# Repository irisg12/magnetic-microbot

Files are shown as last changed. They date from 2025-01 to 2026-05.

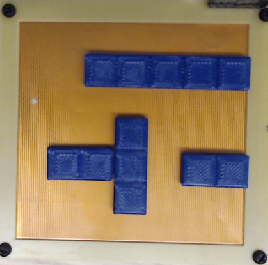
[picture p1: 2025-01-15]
MATLAB/TeamImage2.png

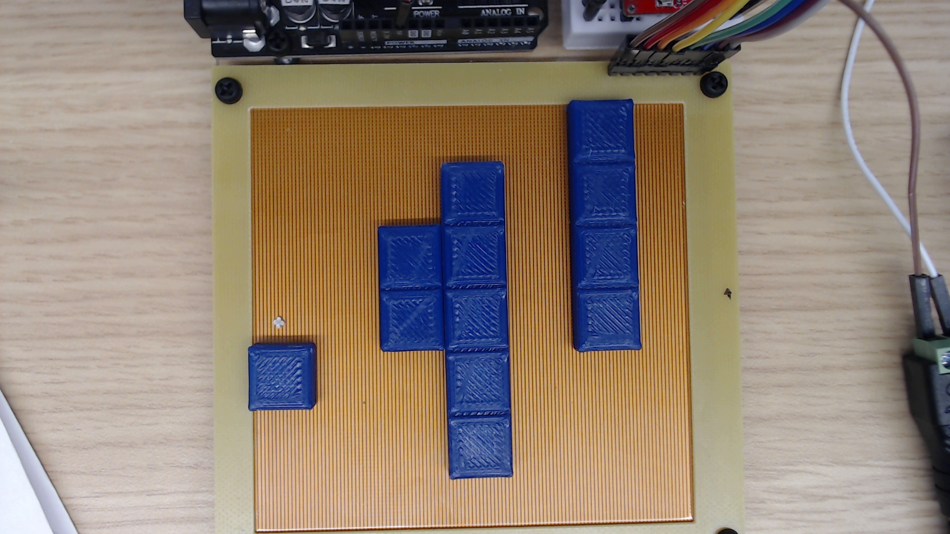
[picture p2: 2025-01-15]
MATLAB/TeamImage1.jpg

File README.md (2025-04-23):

# magnetic-microrobot

Magnetic microrobot manipulation system that adapts a flex PCB platform inspired by the Hackaday “2D Stepper Motor Etched on PCB” project.

## Overview

This repository contains code, schematics, and CAD files for a mm-scale magnetic robot control platform designed for open and closed loop trajectory execution, computer vision robot tracking, and micromanipulation.

The system uses a two-layer flex PCB with orthogonal serpentine traces powered by two stepper motor drivers. The resulting configuration generates magnetic fields that allow a mm-scale magnet placed on the PCB to be manipulated in 8 directions. 

## Features 

- Live tracking of robot and obstacle positions for closed-loop control and image processing
- Direction control and motor driver actuation via Arduino serial communication
- MATLAB A* pathfinding algorithm and visualization for trajectory planning and obstacle avoidance 

### Included Files

- FLEX PCB Gerber Files for manufacturing
- DXF file for acrylic base with cutouts for PCB mounting and wiring
- STL files for obstacles and manipulation payloads 

## Requirements

- MATLAB Support Package for USB Webcams
- MATLAB Image Processing Toolbox

## File Organization

- Upload microbot_multidirection_serial.ino to Arduino Uno

## Hardware Components 

- Flex PCB with stiffener
- N52 disk magnets: 1mm x 0.5mm (4 ct) and 3mm x 1mm (1 ct)
- Arduino Uno
- 170 pin breadboard
- A4988 Stepper Motor Drivers (2 ct)
- 3/16" thick acrylic sheet: each base has approximate dimensions 4.2" x 5.9" 
- M3 nuts and bolts for mounting 
- Webcam & webcam stand

## Wiring Schematic
Default pin connections for Arduino, motor drivers, and PCB also available in SetupSchematic.svg. Drivers are full-stepping, which results in the smoothest motion.

Schematic

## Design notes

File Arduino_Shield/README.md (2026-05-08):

# Arduino shield for platform system

This folder contains relevant files for an Arduino motor shield to control each platform.

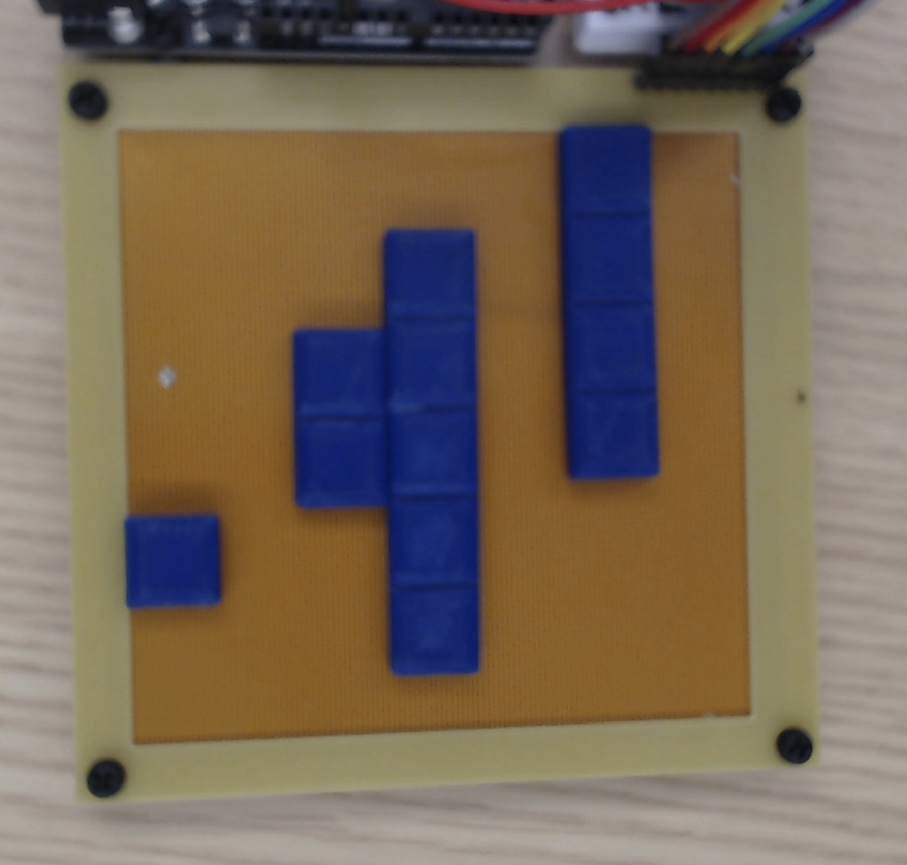
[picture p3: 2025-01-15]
MATLAB/TeamImage3.jpg

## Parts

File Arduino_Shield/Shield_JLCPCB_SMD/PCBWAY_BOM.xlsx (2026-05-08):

 |  |  | xxxx xxxx xxxxx xxPCS BOM (Sample Bill of Materials)
Item # | *Designator | *Qty | Manufacturer | *Mfg Part # | Description / Value | *Package/Footprint | Type | Your Instructions / Notes | LCSC Number
1 | C4,C3 | 2 | Honor Elec | RVT1E101M0607 | CAP-SMD_BD6.3-L6.6-W6.6-LS7.2-R-RD | SMD | SMD | 100uF | C3338
2 | J1,J4 | 2 | SparkFun | PRT-11417 | PinSocket_1x08_P2.54mm_Vertical | 8POS | thru-hole | Arduino Header Kit - Power
3 | J3 | 1 | SparkFun | PRT-11417 | PinSocket_1x06_P2.54mm_Vertical | 6POS | thru-hole | Arduino Header Kit - Analog
4 | J2 | 1 | SparkFun | PRT-11417 | PinSocket_1x10_P2.54mm_Vertical | 10POS | thru-hole | Arduino Header Kit - Digita/PWM
5 | C1,C2 | 2 | Samsung Electro-Mechanics | CL21B104KCFNNNE | C_0805_2012Metric | 0805 | SMD | .1uF | C28233
6 | J5 | 1 | XKB Connection | DC-018-2.5A-2.5 | DC-IN-TH_DC-018 |  | thru-hole | Barrel Jack | C2880553
7 | LR1,LR2,UD2,UD1 | 4 | BOOMELE | 2.54-1*8P | PinSocket_1x08_P2.54mm_Vertical | 8POS | thru-hole | 1x8 | C27438
8 | X1,Y1 | 2 | XFCN | PZ254V-11-04P | PinHeader_1x04_P2.54mm_Vertical | 4POS | thru-hole | 1x4 Pin | C492403

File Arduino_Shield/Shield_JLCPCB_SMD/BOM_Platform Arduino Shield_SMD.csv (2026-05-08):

Id | Designator | Footprint | Quantity | Designation | Supplier and ref
1 | C4,C3 | C_1206_3216Metric | 2 | 100uF
2 | J1 | PinSocket_1x08_P2.54mm_Vertical | 1 | Power
3 | J3 | PinSocket_1x06_P2.54mm_Vertical | 1 | Analog
4 | J2 | PinSocket_1x10_P2.54mm_Vertical | 1 | Digital/PWM
5 | J4 | PinSocket_1x08_P2.54mm_Vertical | 1 | Digital/PWM
6 | C1,C2 | C_0805_2012Metric | 2 | .1uF
7 | J5 | BarrelJack_Horizontal | 1 | Barrel_Jack_MountingPin
8 | LR1,LR2,UD2,UD1 | PinSocket_1x08_P2.54mm_Vertical | 4 | Conn_01x08
9 | X1,Y1 | PinHeader_1x04_P2.54mm_Vertical | 2 | Conn_01x04_Pin

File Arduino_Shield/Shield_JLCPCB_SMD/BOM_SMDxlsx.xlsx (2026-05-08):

Id | Designator | Footprint | Quantity | Designation | JLCPCB Part #
1 | C4,C3 | CAP-SMD_BD6.3-L6.6-W6.6-LS7.2-R-RD | 2 | 100uF | C3338
2 | J1,J4 | PinSocket_1x08_P2.54mm_Vertical | 1 | Power | C27438
3 | J3 | PinSocket_1x06_P2.54mm_Vertical | 1 | Analog | C2935900
4 | J2 | PinSocket_1x10_P2.54mm_Vertical | 1 | Digital/PWM | C350306
5 | C1,C2 | C_0805_2012Metric | 2 | .1uF | C28233
6 | J5 | DC-IN-TH_DC-018 | 1 | Barrel_Jack_MountingPin | C2880553
7 | LR1,LR2,UD2,UD1 | PinSocket_1x08_P2.54mm_Vertical | 4 | Conn_01x08 | C27438
8 | X1,Y1 | PinHeader_1x04_P2.54mm_Vertical | 2 | Conn_01x04_Pin | C492403

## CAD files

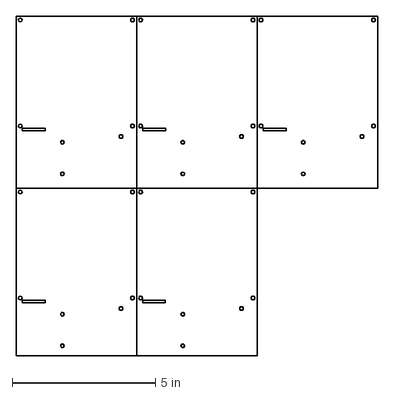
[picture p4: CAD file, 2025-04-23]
Acrylic Laser Cut 5ct - Iris.dxf
12.6 x 11.8 in

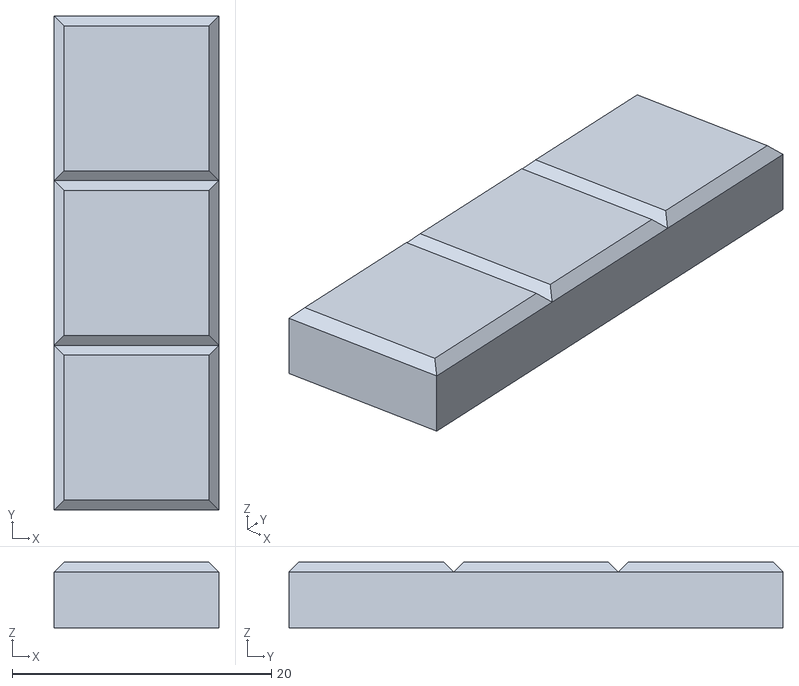
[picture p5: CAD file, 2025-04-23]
CAD_Models/obstacle_3bit.stl
12.7 x 38.1 x 5.08

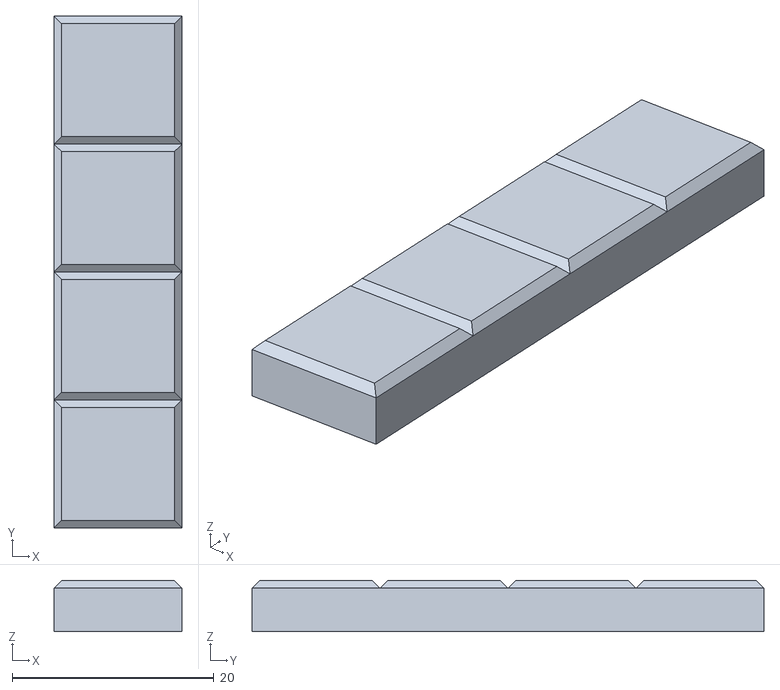
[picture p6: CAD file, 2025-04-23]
CAD_Models/obstacle_4bit.stl
12.7 x 50.8 x 5.08

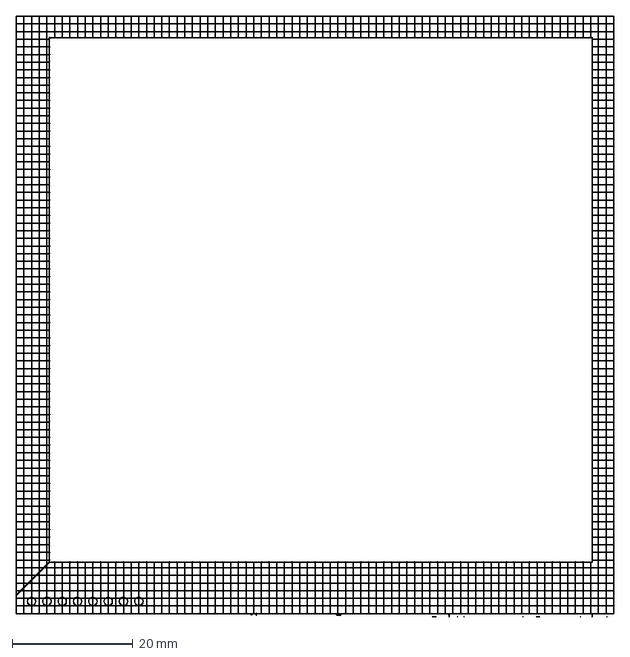
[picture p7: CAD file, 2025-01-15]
FLEX PCB Stiffener Border DXF.dxf
99.1 x 99.7 mm

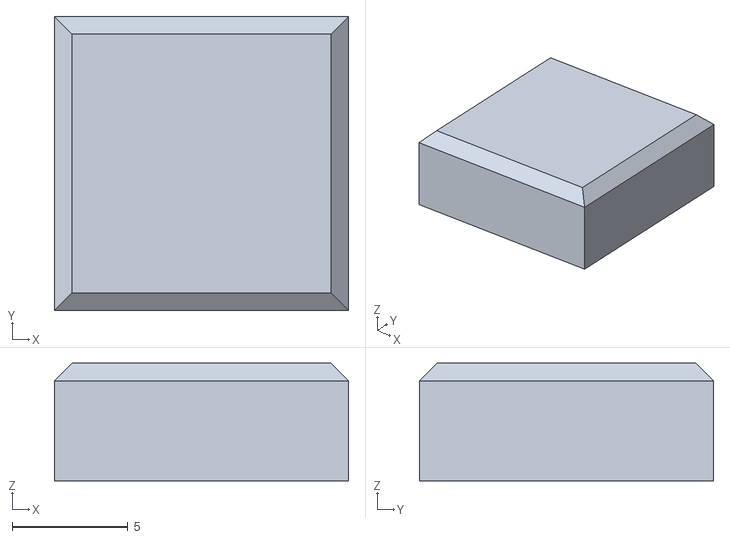
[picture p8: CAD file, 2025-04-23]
CAD_Models/obstacle_1bit.stl
12.7 x 12.7 x 5.08

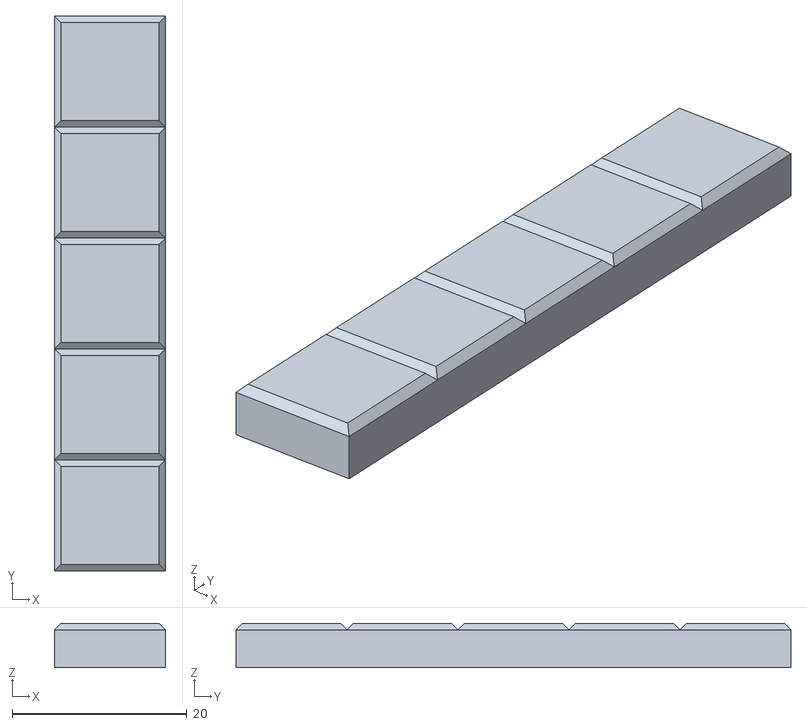
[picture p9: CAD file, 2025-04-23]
CAD_Models/obstacle_5bit.stl
12.7 x 63.5 x 5.08

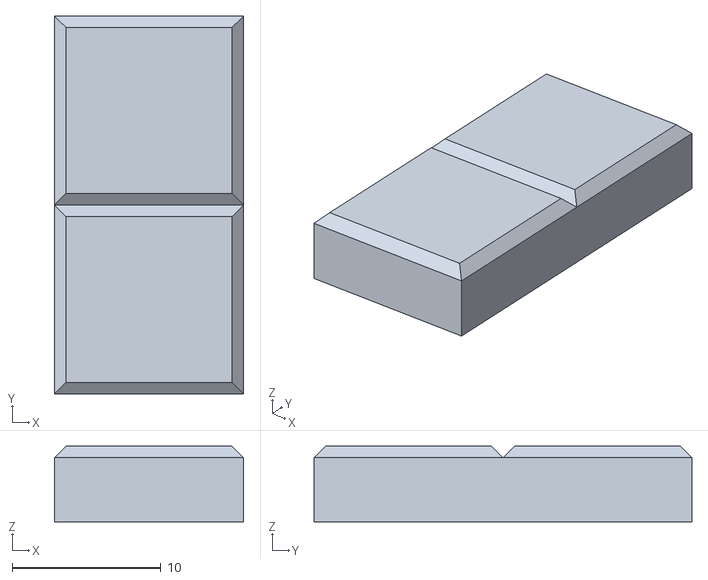
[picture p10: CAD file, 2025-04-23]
CAD_Models/obstacle_2bit.stl
12.7 x 25.4 x 5.08

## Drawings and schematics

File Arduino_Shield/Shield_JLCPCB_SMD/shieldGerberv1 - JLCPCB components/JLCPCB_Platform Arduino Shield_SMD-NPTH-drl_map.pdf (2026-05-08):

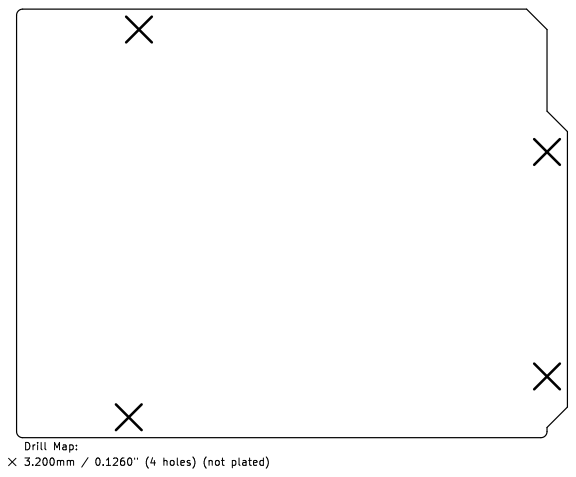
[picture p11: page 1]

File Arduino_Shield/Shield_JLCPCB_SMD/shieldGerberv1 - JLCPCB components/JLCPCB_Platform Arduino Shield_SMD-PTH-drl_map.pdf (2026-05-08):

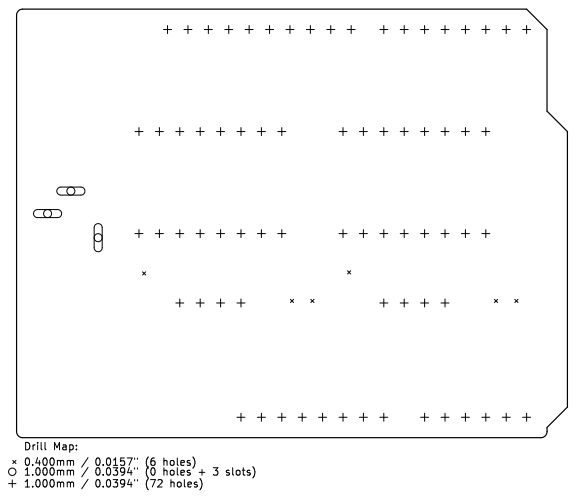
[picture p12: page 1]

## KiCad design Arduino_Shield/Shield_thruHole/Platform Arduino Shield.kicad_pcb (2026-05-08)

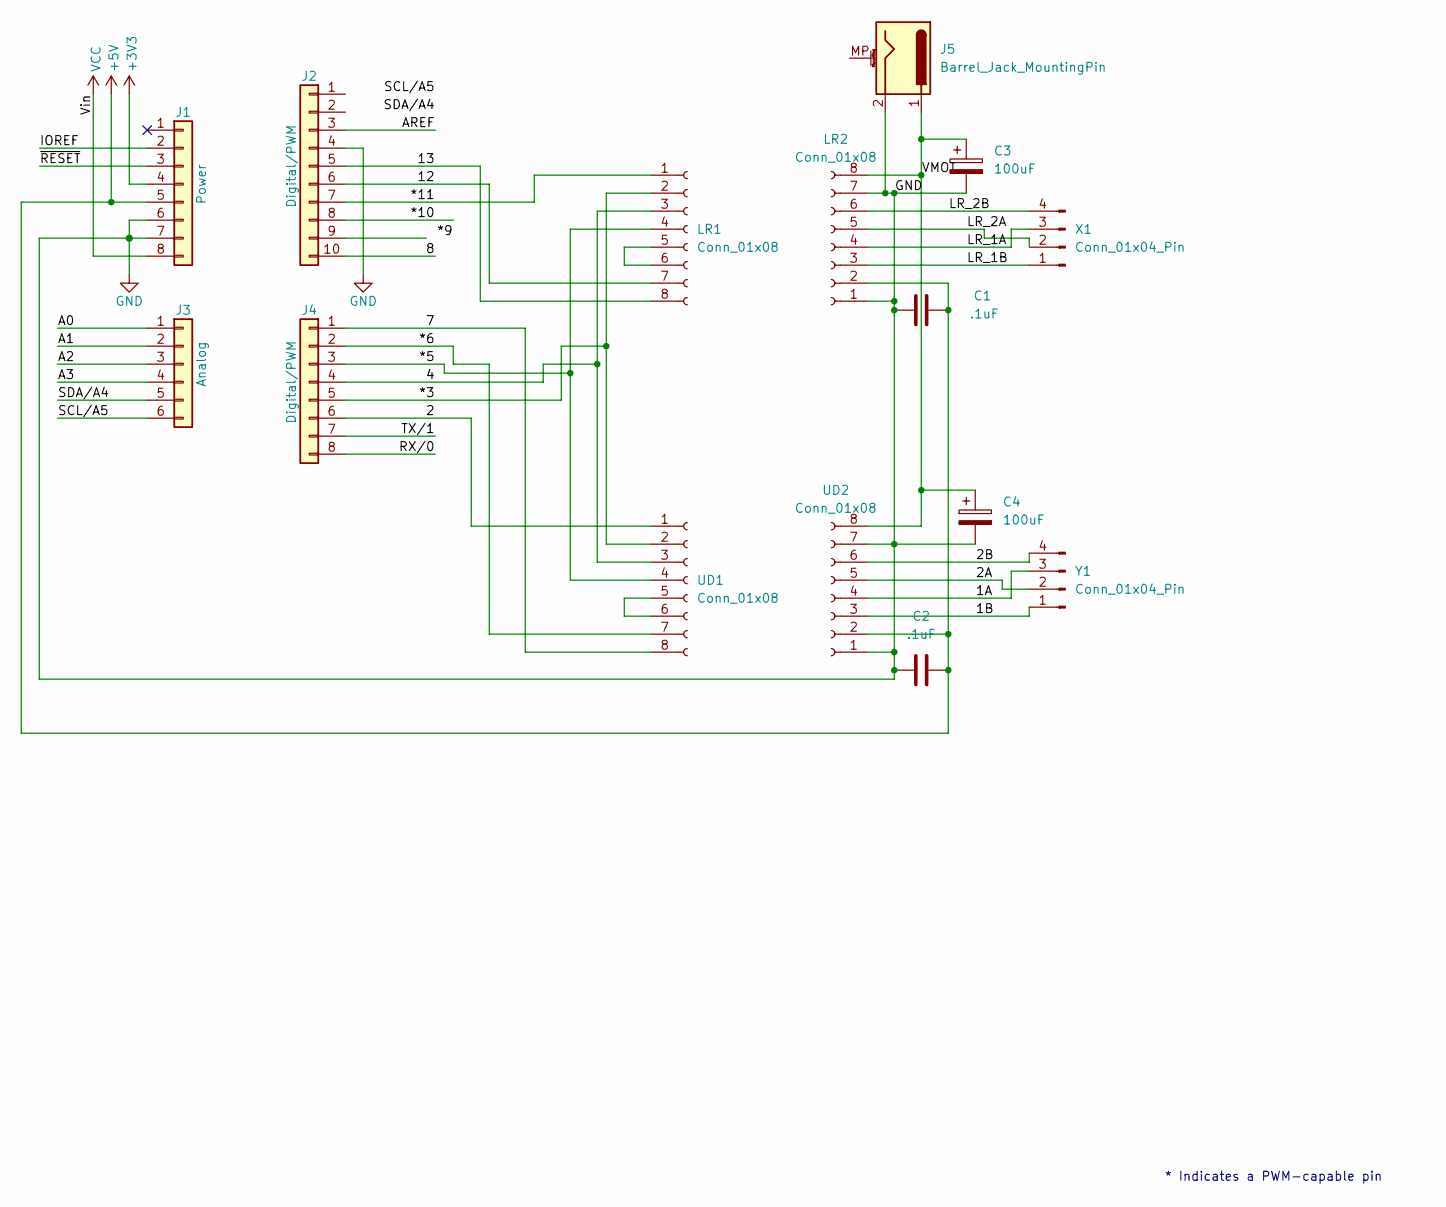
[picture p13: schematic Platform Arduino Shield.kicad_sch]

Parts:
C1, C2: .1uF; C_Disc_D5.0mm_W2.5mm_P5.00mm
C3, C4: 100uF; CP_Radial_D6.3mm_P2.50mm
J1: Power; PinSocket_1x08_P2.54mm_Vertical
J2: Digital/PWM; PinSocket_1x10_P2.54mm_Vertical
J3: Analog; PinSocket_1x06_P2.54mm_Vertical
J4: Digital/PWM; PinSocket_1x08_P2.54mm_Vertical
J5: Barrel_Jack_MountingPin; BarrelJack_Horizontal
LR1, LR2: Conn_01x08; PinSocket_1x08_P2.54mm_Vertical
UD1, UD2: Conn_01x08; PinSocket_1x08_P2.54mm_Vertical
X1: Conn_01x04_Pin; PinHeader_1x04_P2.54mm_Vertical
Y1: Conn_01x04_Pin; PinHeader_1x04_P2.54mm_Vertical

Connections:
+3V3: J1.4
+5V: C1.2, C2.2, J1.5, LR2.2, UD2.2
/1A: UD2.4, Y1.3
/1B: UD2.3, Y1.1
/2: J4.6, UD1.1
/2A: UD2.5, Y1.2
/2B: UD2.6, Y1.4
/4: J4.4, LR1.3, UD1.3
/7: J4.1, UD1.8
/8: J2.10
/12: J2.6, LR1.7
/13: J2.5, LR1.8
/*3: J4.5, LR1.2, UD1.2
/*5: J4.3, LR1.4, UD1.4
/*6: J4.2, UD1.7
/*10: J2.8
/*11: J2.7, LR1.1
/A0: J3.1
/A1: J3.2
/A2: J3.3
/A3: J3.4
/AREF: J2.3
/IOREF: J1.2
/LR_1A: LR2.4, X1.3
/LR_1B: LR2.3, X1.1
/LR_2A: LR2.5, X1.2
/LR_2B: LR2.6, X1.4
/RX/0: J4.8
/SCL/A5: J3.6
/SDA/A4: J3.5
/TX/1: J4.7
/VMOT: C3.1, C4.1, J5.1, LR2.8, UD2.8
/~RESET: J1.3
GND: C1.1, C2.1, C3.2, C4.2, J1.6, J1.7, J2.4, J5.2, LR2.1, LR2.7, UD2.1, UD2.7
unnamed: LR1.5, LR1.6
unnamed: UD1.5, UD1.6
VCC: J1.8

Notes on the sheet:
* Indicates a PWM-capable pin

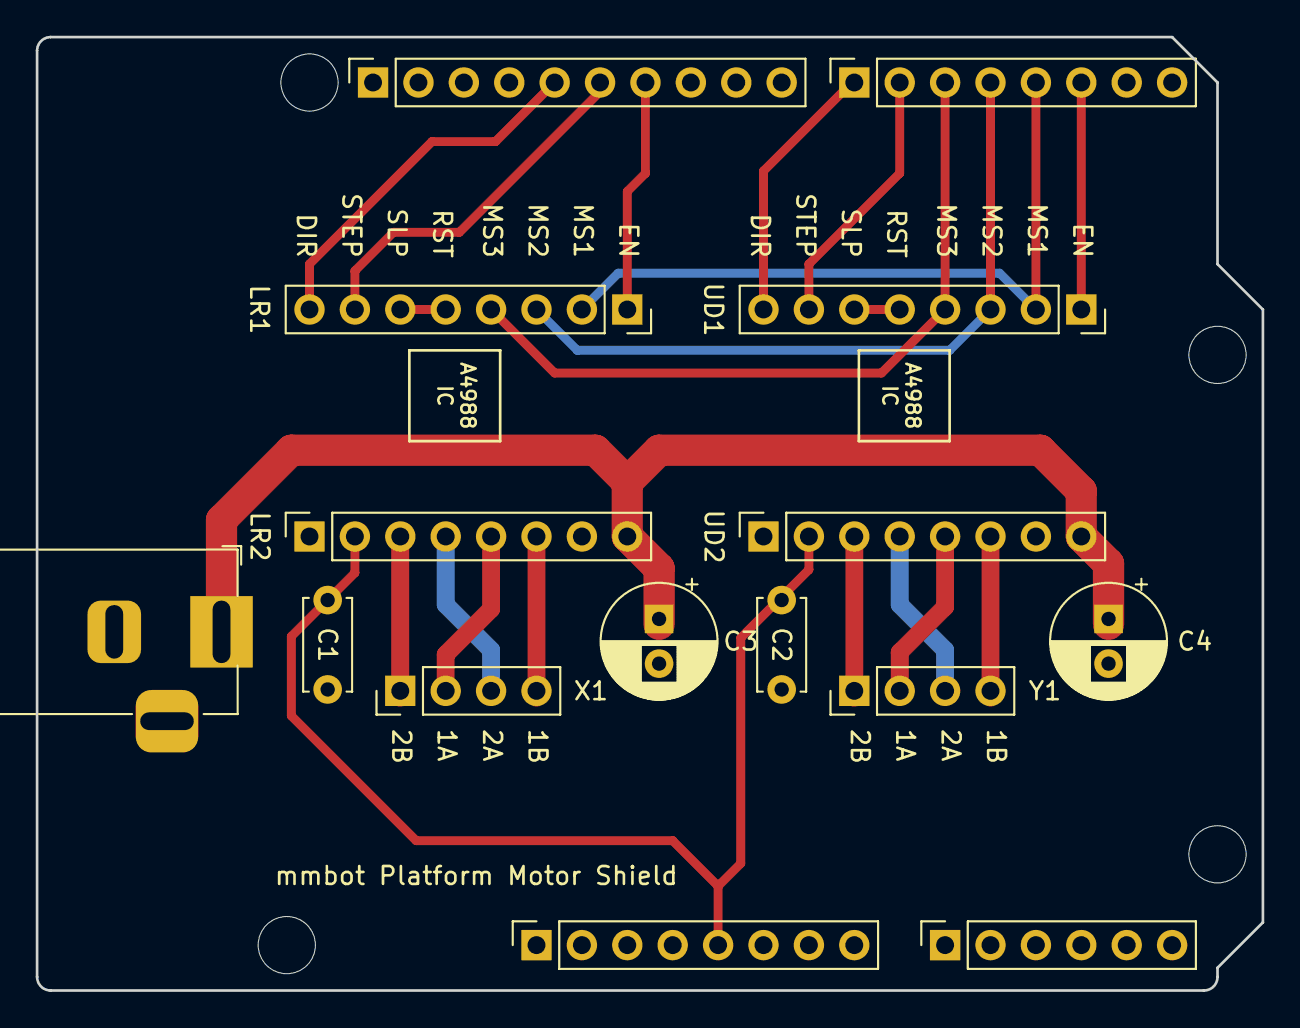
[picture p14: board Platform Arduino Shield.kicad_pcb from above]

Board: 2 copper layers, 68.6 x 53.3 mm, 19 parts (0 on the bottom side), 22 nets.

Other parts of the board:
MH1, MH2, MH3, MH4: MountingHole_3.2mm

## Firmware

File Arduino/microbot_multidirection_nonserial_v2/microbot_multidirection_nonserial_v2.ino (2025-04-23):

// Arduino only looping test of all 8 directions 
// Commands sent directly to drivers, no MATLAB serial comm
// v2 allows for easy changes to command order and counts for each direction
// pauses in between direction changes are automatically added

// Vertical and horizontal movement represented by the four cardinal directions NSEW
// diagonal movements: A is northwest, B is northeast, C is southeast, D is southwest
// X represents default case (no movement) 
// F represents full command set completion (relevant for MATLAB serial comm)

/* Setup */
// 1x8 header pins should be at the top right of the PCB board
// see Github schematic: pins 1-4 control U/D movement, pins 5-8 control L/R movement

#define UDStepPin 2     // pin to control up/down step timing
#define UDDirPin 3      // direction indicator: N = LOW, S = HIGH
#define UDEnablePin 4   // active low enable

#define LRStepPin 9     // pin to control left/right step timing
#define LRDirPin 10     // direction indicator: E = LOW, W = HIGH
#define LREnablePin 11  // active low enable
#define speed 30        // milliseconds between each L-H or H-L transition

void setup() {
  pinMode(UDStepPin, OUTPUT);
  pinMode(UDDirPin, OUTPUT);
  pinMode(LRStepPin, OUTPUT);
  pinMode(LRDirPin, OUTPUT);
  pinMode(UDEnablePin, OUTPUT);
  pinMode(LREnablePin, OUTPUT);
}

void loop() 
{
  int mult = 2; // # of sets of 10 steps each direction repeats for
  int num = 9;  // number of commands, length of char array commands
  
  int n = 10 * mult;
  int s = 10 * mult;
  int e = 10 * mult;
  int w = 10 * mult;
  int a = 10 * mult; 
  int b = 10 * mult; 
  int c = 10 * mult; 
  int d = 10 * mult; 
  int x = 3 * mult;  // 3 step pause between direction changes
  int f = 1;         // terminating character
  int length = n+s+e+w+a+b+c+d+f+x*num; // total command set length

  // directions to execute in order
  char commands[num] =   {'N', 'E', 'S', 'W', 'A', 'B', 'C', 'D', 'F'}; 
  // number of repetitions per character
  int commandcounts[num] = {n, e, s, w, a, b, c, d, f};
  char dir[length];

  int totalchars = 0;
  // populating the char array dir with all commands separated by pauses
  for (int i = 0; i < num; i++) {
    for (int j = 0; j < commandcounts[i]; j++) {
      dir[totalchars++] = commands[i];
    } 
    for (int jx = 0; jx < x; jx++) {
      dir[totalchars++] = 'X';
    }
  }
  
  char direction; // current direction
  for (int i = 0; i < length; i++) {
    direction = dir[i];
    digitalWrite(UDEnablePin, LOW);
    digitalWrite(LREnablePin, LOW);
    switch(direction) {
      case 'N':
        digitalWrite(UDDirPin, LOW);
        digitalWrite(LREnablePin, HIGH);
        break;
      case 'S':
        digitalWrite(UDDirPin, HIGH);
        digitalWrite(LREnablePin, HIGH);
        break;
      case 'W':
        digitalWrite(LRDirPin, HIGH);
        digitalWrite(UDEnablePin, HIGH);
        break;
      case 'E':
        digitalWrite(LRDirPin, LOW);
        digitalWrite(UDEnablePin, HIGH);
        break;
      case 'A':
        digitalWrite(UDDirPin, LOW);
        digitalWrite(LRDirPin, HIGH);
        break;
      case 'B':
        digitalWrite(UDDirPin, LOW);
        digitalWrite(LRDirPin, LOW);
        break;
      case 'C':
        digitalWrite(UDDirPin, HIGH);
        digitalWrite(LRDirPin, LOW);
        break;
      case 'D':
        digitalWrite(UDDirPin, HIGH);
        digitalWrite(LRDirPin, HIGH);
        break;
      case 'F':
        Serial.println("Target reached");
        //Serial.flush();
      default:
        digitalWrite(UDEnablePin, HIGH);
        digitalWrite(LREnablePin, HIGH);
        break;
    }
    digitalWrite(UDStepPin, HIGH);
    digitalWrite(LRStepPin, HIGH);
    delay(speed); 
    digitalWrite(UDStepPin, LOW);
    digitalWrite(LRStepPin, LOW);
    delay(speed); 
  }
  delay(4000); // delay for 4 seconds between loops
}

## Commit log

2025-04-23 Add files via upload
    File upload for acrylic mounting board and obstacles
    [Acrylic Laser Cut 5ct - Iris.dxf, obstacle_1bit.stl, obstacle_2bit.stl, obstacle_3bit.stl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]
2025-04-23 Uploaded wiring schematic
2025-04-30 organized CAD files and updated Arduino code
    [obstacle_1bit.stl, obstacle_2bit.stl, obstacle_3bit.stl, obstacle_4bit.stl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]
2026-05-08 upload shield files
    [BOM_Platform Arduino Shield_SMD.csv, BOM_SMDxlsx.xlsx, JLCPCB_Platform Arduino Shield_SMD-B_Cu.gbr, JLCPCB_Platform Arduino Shield_SMD-B_Mask.gbr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]
